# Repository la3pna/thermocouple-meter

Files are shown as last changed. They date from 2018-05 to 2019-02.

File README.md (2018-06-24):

View this project on [CADLAB.io](https://cadlab.io/project/1066). 

# thermocouple-meter
a open source thermocouple meter

This project runs on the Empyrean series ARM microcontroller boards. It may run on Arduino Zero and other SAMD series, but it will not run on ATMEGA series boards!

Todo:
PCB:
* do a PCB for the 2 sensors 3 and 4
* ESP-01 wlan alternative? (as of now there is a extra serial on the board.)
* GPIB? (using the extra serial port?)

SCPI Commands:
   *  *IDN?                  -> identify
   *  *RST                   -> reset to local
   *  :TRIGger
       *    :SINGle          -> trigger single
       *    :CONTinous       -> trigger continous
   *  :MEASure
       *    :TEMPerature?    -> get all temp
       *    :TEMPerature1?   -> get temp1
       *    :TEMPerature2?   -> get temp2
       *    :TEMPerature3?   -> get temp3
       *    :TEMPerature4?   -> get temp4
       *    :INTernal1?      -> get int1 (compensation temperature)
       *    :INTernal2?      -> get int2
       *    :INTernal3?      -> get int3
       *    :INTernal4?      -> get int4
   *  :SYStem
       *    :VOLTage?        -> get supply voltage
       *    :ERRor?          -> get/clears error from error handling
       *    :PRINT           -> display print string
   *  :UNIT *(getting these to work will require rewriting the adafruit library from scratch)*
       *    :TEMPerature     -> set_temperature_unit (C/CEL/F/FAR/K/KEL) *NOT IMPLEMENTED YET* 
       *    :TEMPerature?    -> get_temprature unit (C/CEL/F/FAR/K/KEL) *NOT IMPLEMENTED YET*
       
 Libraries needed: 
   - U8g2lib (Available in arduino library manager)
   - Open Instrument control [scpiparser] ( https://github.com/la3pna/oic )
   - Adafruit MAX31855 (available in arduino library manager) (intend to rewrite this to use some SAMD features in getting the data) 
   
   Bevare that there is some fake MAX31855 on the marked that does not work! Make sure you get your MAX31855 and thermocouples from a reputable source to avoid problems.

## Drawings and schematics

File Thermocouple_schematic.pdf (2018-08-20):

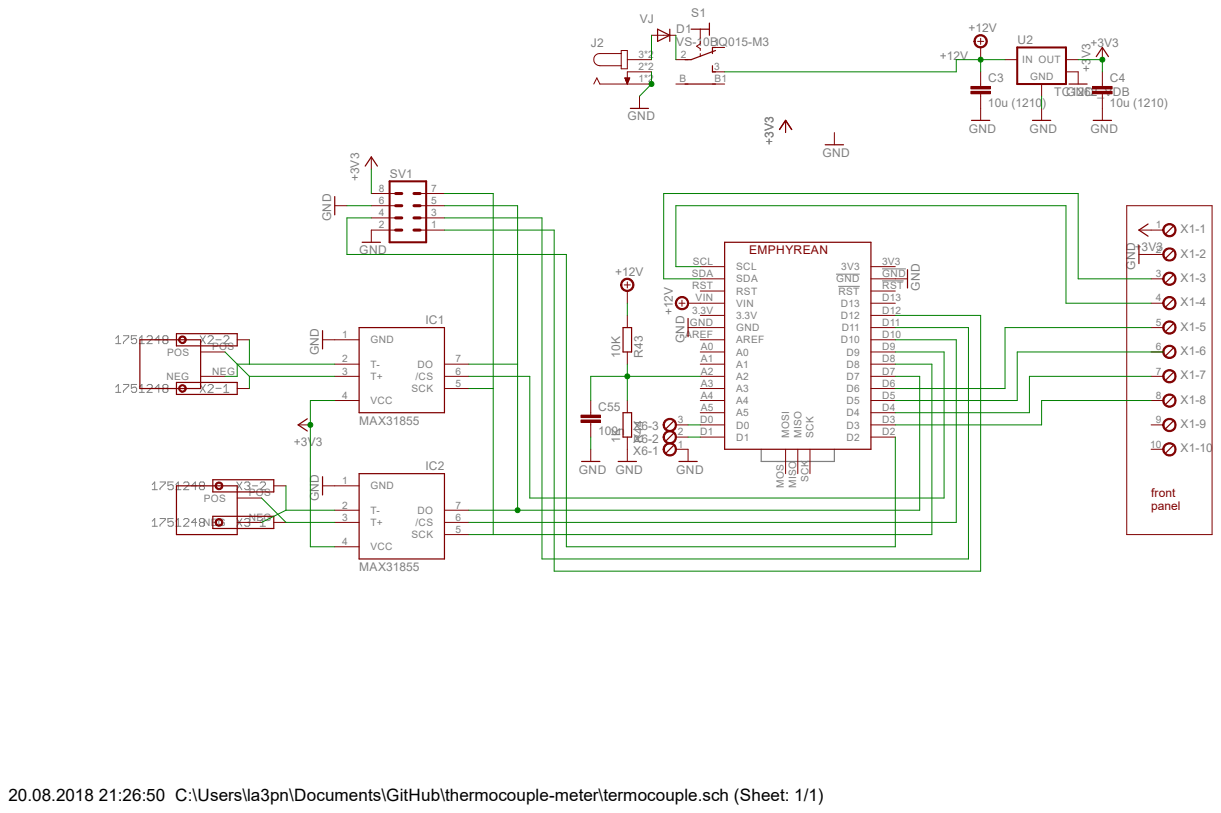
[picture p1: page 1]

20.08.2018 21:26:50 C:\Users\la3pn\Documents\GitHub\thermocouple-meter\termocouple.sch (Sheet: 1/1)

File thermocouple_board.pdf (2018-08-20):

44.45

22.86

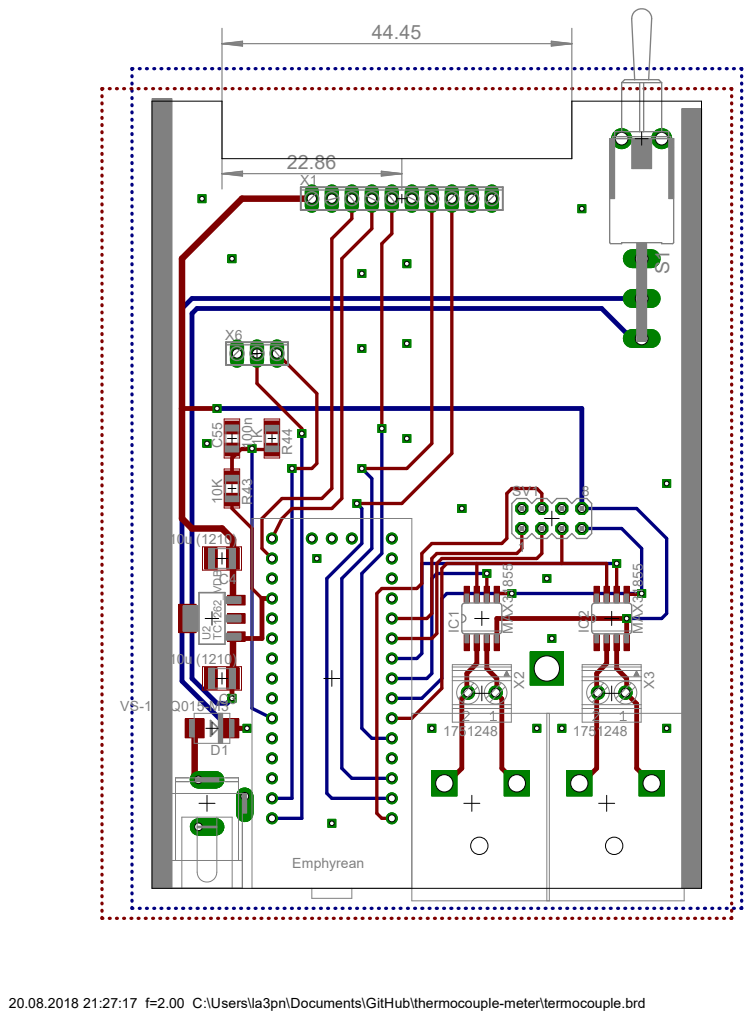
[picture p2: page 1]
Emphyrean; 8 IC¹; IC²; X1 R⁴³; R⁴⁴ C⁵⁵ U²; SV1 MAX³¹⁸⁵⁵; MAX³¹⁸⁵⁵ ¹⁰K; 100n 1K TC¹²⁶²_VDB

20.08.2018 21:27:17 f=2.00 C:\Users\la3pn\Documents\GitHub\thermocouple-meter\termocouple.brd

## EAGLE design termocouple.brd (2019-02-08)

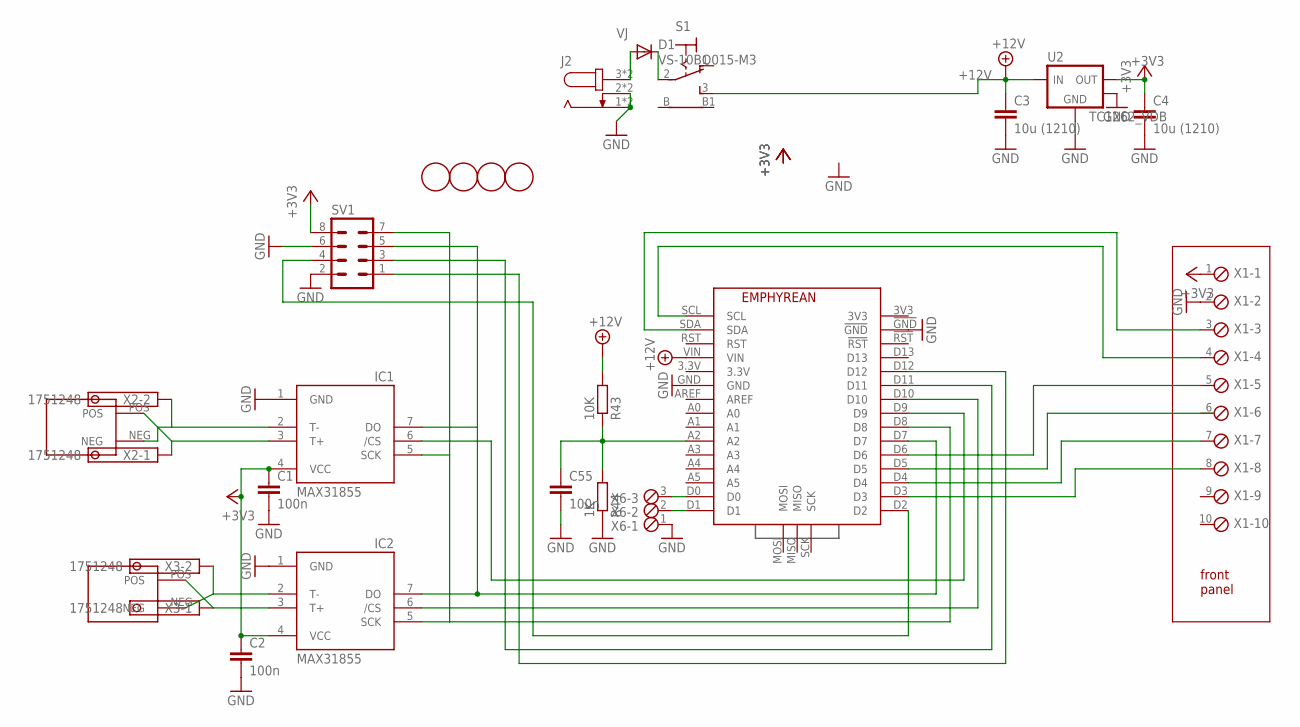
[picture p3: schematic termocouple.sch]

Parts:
C1, C2, C55: 100n; C1206
C3, C4: 10u (1210); C1210
D1: VS-10BQ015-M3; SMB
IC1, IC2: MAX31855; SO08
J2: JACK-PLUG; SPC4078
R43: 10K; R1206
R44: 1K; R1206
S1: LPV-1
SV1: MA04-2
U2: TC1262_VDB; SOT-223-3
U$1: EPHYREAN; EMPHYREAN
U$2, U$3: THERMOCOUPLE
U$4, U$5, U$6, U$7: FIDUCIAL; FIDUCIAL_1MM
X1: MPT10; 10POL254
X2, X3: 1751248
X6: MPT3; 3POL254

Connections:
+3V3: C1.1, C2.1, C4.1, IC1.4 (VCC), IC2.4 (VCC), SV1.8, U2.3 (VOUT), X1.1
+12V: C3.1, R43.2, S1.3 (S), U2.1 (VIN), U$1.VIN
GND: C1.2, C2.2, C3.2, C4.2, C55.2, IC1.1 (GND), IC2.1 (GND), J2.1, J2.2, J2.4 (1), J2.5 (2), R44.1, SV1.2, SV1.6, U2.2 (GND), U2.4 (TAB), U$1.!GND, U$1.GND, X1.2, X6.1
unnamed: IC1.7 (DO), IC2.7 (DO), SV1.5, U$1.D7
unnamed: IC1.5 (SCK), IC2.5 (SCK), SV1.7, U$1.D8
unnamed: IC2.6 (/CS), U$1.D10
unnamed: IC1.6 (/CS), U$1.D9
unnamed: U$1.SDA, X1.3
unnamed: SV1.3, U$1.D11
unnamed: U$1.SCL, X1.4
unnamed: U$1.D6, X1.5
unnamed: U$1.D4, X1.7
unnamed: U$1.D3, X1.8
unnamed: D1.C, S1.2
unnamed: SV1.1, U$1.D12
unnamed: SV1.4, U$1.D2
unnamed: IC2.3 (T+), U$2.POS, X3.1
unnamed: IC2.2 (T-), U$2.NEG, X3.2
unnamed: IC1.3 (T+), U$3.POS, X2.1
unnamed: IC1.2 (T-), U$3.NEG, X2.2
unnamed: U$1.D0, X6.3
unnamed: U$1.D1, X6.2
unnamed: C55.1, R43.1, R44.2, U$1.A2
VJ: D1.A, J2.3, J2.6 (3)

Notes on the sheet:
front panel

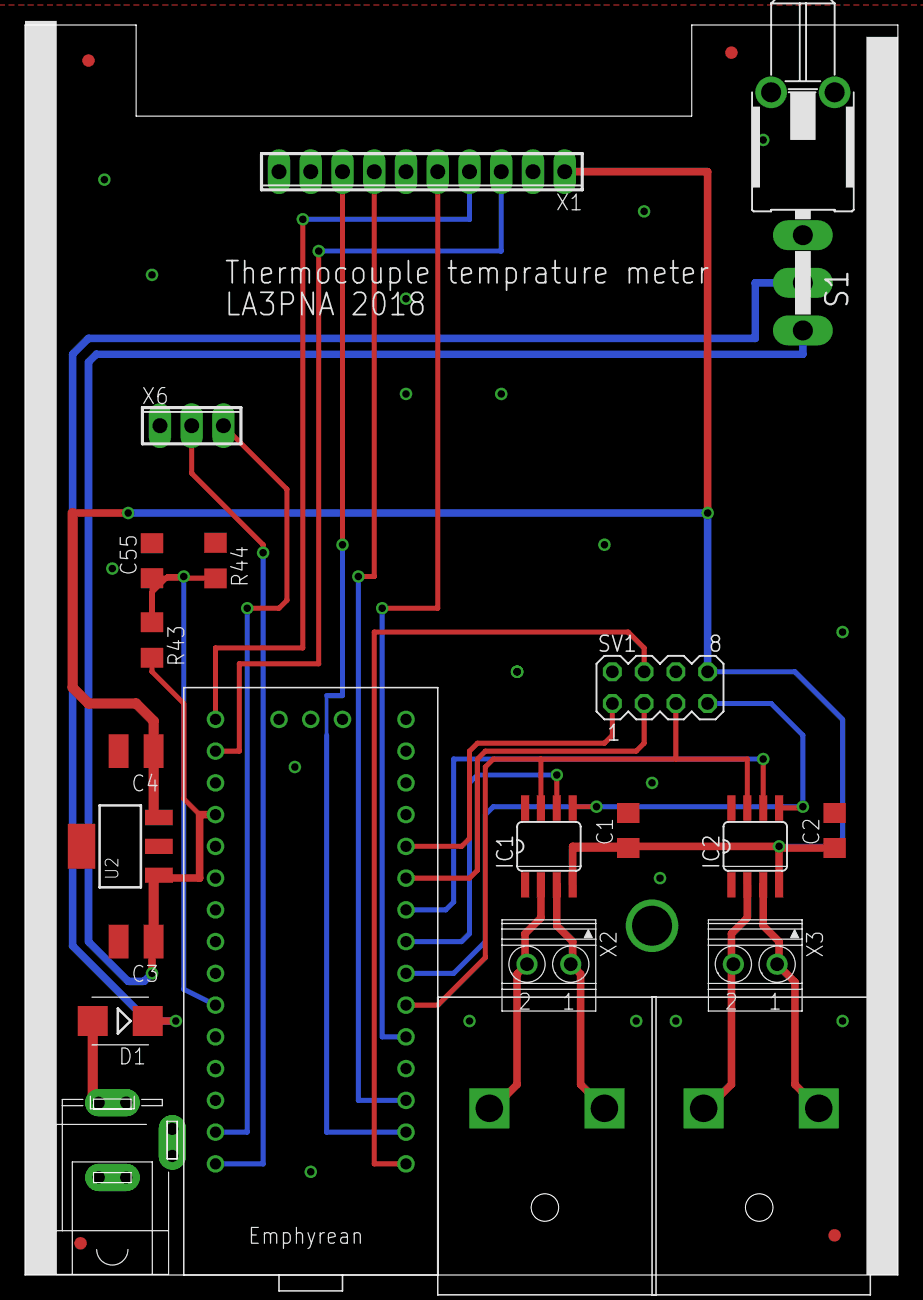
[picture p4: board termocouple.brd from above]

Board: 2 copper layers, 69.8 x 100.0 mm, 25 parts (0 on the bottom side), 24 nets.

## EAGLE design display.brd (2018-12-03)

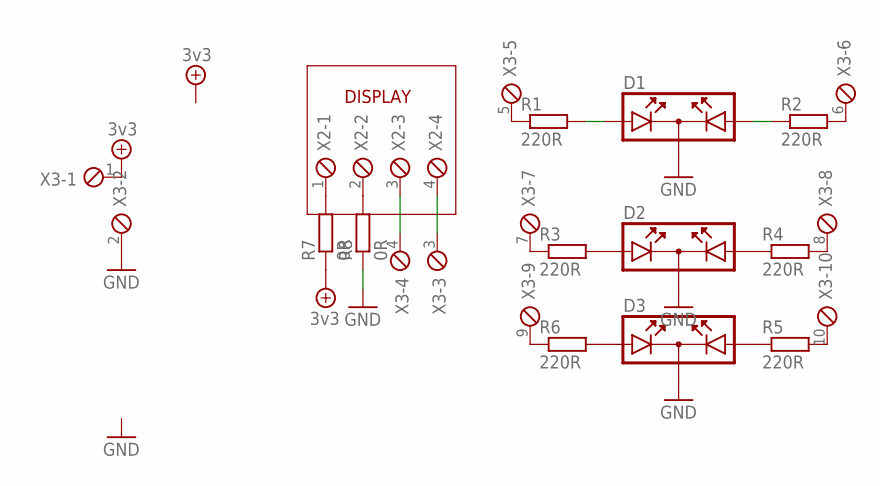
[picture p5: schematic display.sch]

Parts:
D1, D2, D3: DUOLED
R1, R2, R3, R4, R5, R6: 220R; R0603
R7, R8: 0R; R0603
X2: MPT4; 4POL254
X3: MPT10; 10POL254

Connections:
+UB: R7.1, X3.1
GND: D1.K, D2.K, D3.K, R8.1, X3.2
unnamed: D1.A1, R1.2
unnamed: D1.A2, R2.1
unnamed: X2.3, X3.4
unnamed: X2.4, X3.3
unnamed: R1.1, X3.5
unnamed: R2.2, X3.6
unnamed: D2.A1, R3.2
unnamed: D2.A2, R4.1
unnamed: D3.A2, R5.1
unnamed: D3.A1, R6.2
unnamed: R3.1, X3.7
unnamed: R4.2, X3.8
unnamed: R6.1, X3.9
unnamed: R5.2, X3.10
unnamed: R7.2, X2.1
unnamed: R8.2, X2.2

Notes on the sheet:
DISPLAY

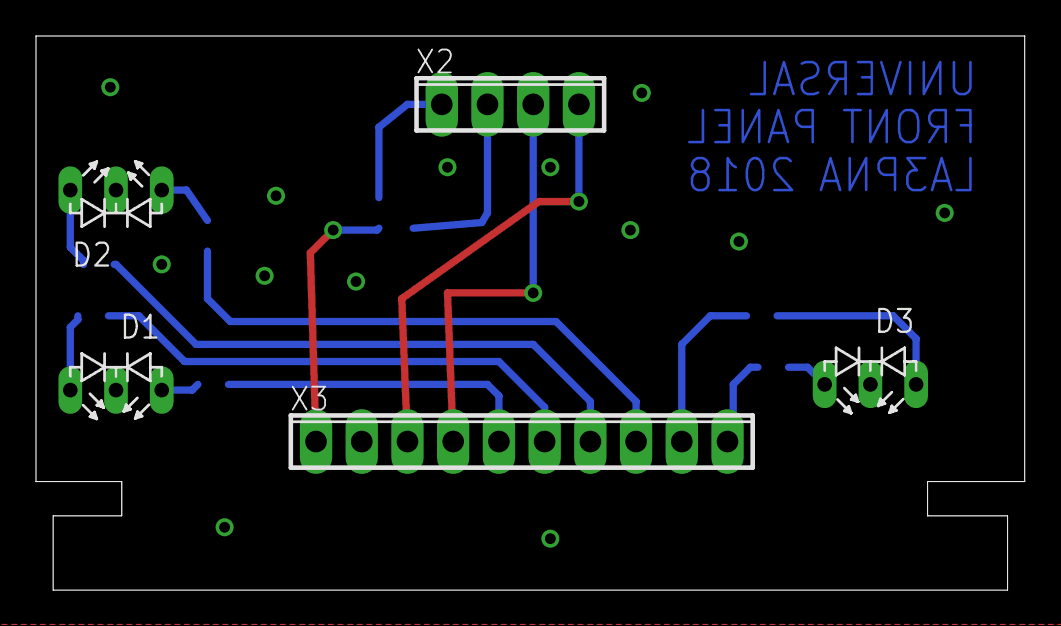
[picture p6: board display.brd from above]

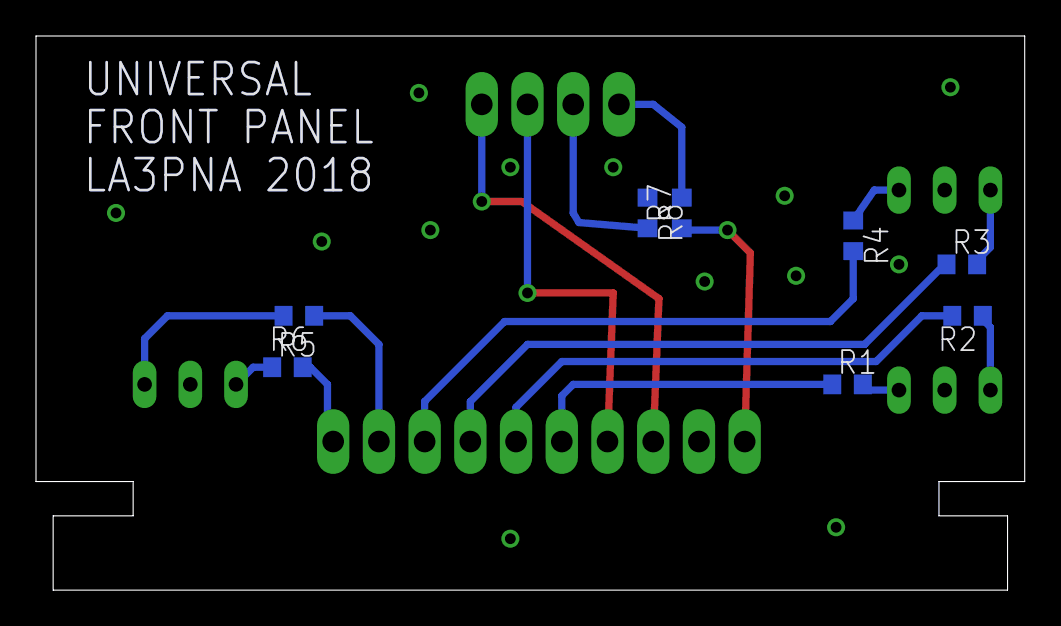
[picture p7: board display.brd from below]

Board: 2 copper layers, 54.9 x 30.8 mm, 13 parts (8 on the bottom side), 18 nets.

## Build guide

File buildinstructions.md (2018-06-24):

**Build instructions**

The PCB fits the standard chinese 100 * 76 * 35mm aluminium enclosures available on ebay. 
PCB's and front panels may be available from me, contact me for information. 

* Mount and solder the SMD's on the main PCB. 
* Mount and solder the socket for the SV1 Expantion port if you intend to build the 4 probe version. 
* Fit the 2 thermocouple connectors to the PCB. 
  - Start by opening the connector and remove all screws and nuts. 
  - Mount the connectors to the PCB using 2 M2 screws and the nuts. The screws goes from the connection tab, via the connector and through the PCB. The nut is fitted on the bottom of the PCB. 
* Mount the backpanel to the bottom part of the enclosure. This is to make sure the alignments are correct.
* Fit the headers to the bottom of the PCB. If your Empyrean comes with the headers fitted, skip this step.
* Mount the Empyrean to the top of the PCB, Do not solder it yet.
* Mount the powerjack, but do not solder it yet.  
* Fit the whole PCB assembly into the board, and see that the connectors fits as it should. 
* Adjust the powerjack and Empyrean PCB so that their connectors fit correctly then solder them to the PCB.
* Add the 2 resistors just below the display to the front panel boards. These determine the power connections to the display.
* Solder the angled row connector to the main PCB.
* Slide the display PCB onto the main PCB and solder it in place.
* Mount the power switch to the PCB, but only solder the end pin.
* Cut the display connector row on the solder side so that it does not protude in front of the display. This is to avoid it shorting to the front panel. 
* Mount the display, but do not solder yet.
* Slide the PCB back into the bottom part of the box, and mount the font panel.  
* Holding the display in its connector, adjust it so that it's position is correct, then tack it down and adjust it so its position is correct on the front panel.
* Solder the display and power switch to the PCB.
* Its time to upload the program and test that it works as it should.

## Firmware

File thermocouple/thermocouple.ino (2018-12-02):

/*
 * Thermocouple SCPI Meter by Thomas S. Knutsen LA3PNA. 
 * 
 * 
 * 
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
 */
 
 #include <U8g2lib.h>
 #include <U8x8lib.h>
 #include <avr/dtostrf.h>
 #include <SPI.h>
  #include <scpiparser.h>
 #include "Adafruit_MAX31855.h"

// In this list you define the input voltage resistors in ohm so it measures the input voltage correctly:
float r44 = 2700; // resistor to gnd
float r43 = 30100; // resistor to Vin
 
 
    #define DO   7
    #define CS1   10
    #define CS2   9
    #define CS3   11
    #define CS4   12
    #define CLK  8
    
#if (!defined(__SAMD21G18A__) && !defined(__SAMD21G16A__) && !defined(__SAMD21G16B__) && !defined(__SAMD21J18A__) && !defined(__SAMD21E17A__) && !defined(__SAMD21E18A__))
 #error "This program will only work on SAMD series boards like Empyrean and Zero"
#endif
    
    Adafruit_MAX31855 thermocouple1(CLK, CS1, DO);
    Adafruit_MAX31855 thermocouple2(CLK, CS2, DO);
    Adafruit_MAX31855 thermocouple3(CLK, CS3, DO);
    Adafruit_MAX31855 thermocouple4(CLK, CS4, DO);
    

    
U8G2_SSD1306_128X32_UNIVISION_1_HW_I2C u8g2(U8G2_R0, /* reset=*/ U8X8_PIN_NONE, /* clock=*/ SCL, /* data=*/ SDA);   // pin remapping with ESP8266 HW I2C

struct scpi_parser_context ctx;

scpi_error_t identify(struct scpi_parser_context* context, struct scpi_token* command);
scpi_error_t reset(struct scpi_parser_context* context, struct scpi_token* command);
scpi_error_t get_voltage(struct scpi_parser_context* context, struct scpi_token* command);
scpi_error_t get_temp_1(struct scpi_parser_context* context, struct scpi_token* command);
scpi_error_t get_temp_2(struct scpi_parser_context* context, struct scpi_token* command);
scpi_error_t get_temp_3(struct scpi_parser_context* context, struct scpi_token* command);
scpi_error_t get_temp_4(struct scpi_parser_context* context, struct scpi_token* command);
scpi_error_t set_voltage_2(struct scpi_parser_context* context, struct scpi_token* command);

  float temp1;
  float temp2;
  float temp3;
  float temp4;
 
  boolean contTrigger = true;
  String idString = "LA3PNA,Thermocouple temperature meter,1,0.1A";
  String sendresponse = "";
  String errorstring = "";
  boolean use2 = false;
  int selectpin = 2;
  boolean _verbose = false;

void draw(float temp1, float temp2, float temp3, float temp4 ) {
  // graphic commands to redraw the complete screen should be placed here

  u8g2.firstPage();
  do {
    u8g2.setFont(u8g2_font_ncenB10_tr);
    char buf[12] ="";
    if(use2){
     u8g2.drawStr(0,25,dtostrf(temp1, 4, 2, buf));
    u8g2.drawStr(70,25,dtostrf(temp2, 4, 2, buf));
    u8g2.setFont(u8g2_font_ncenB08_tr);
    u8g2.drawStr(0,8,"1:");
    u8g2.drawStr(70,8,"2:");
    } else{
     u8g2.drawStr(0,14,dtostrf(temp1, 5, 2, buf));
    u8g2.drawStr(70,14,dtostrf(temp2, 5, 2, buf));
    u8g2.drawStr(0,31,dtostrf(temp3, 5, 2, buf));
    u8g2.drawStr(70,31,dtostrf(temp4, 5, 2, buf));
    }
  } while ( u8g2.nextPage() );
}


 
    void setup() {

      pinMode(selectpin,INPUT);
      digitalWrite(selectpin,HIGH); // put on the pullups
      delay(10);
      if(digitalRead(selectpin))
      {
        use2 = true; // select between 2 and 4 sensors
        }
      
      setup_scpi();
       SerialUSB.begin(9600);
       SerialUSB.println("MAX31855 test");
       // wait for MAX chip to stabilize
       Serial1.begin(115200);
       u8g2.begin();
       delay(500);
    }
    
  char line_buffer[256];
  unsigned char read_length;
  int serialport = 0; // 1 = USB, 2 = Serial1, 3 = Serial5;
    
    void loop() {

    // Here we need a routine that selects between the different serial ports, and does some housekeeping so things goes to the correct place
    //
      if (SerialUSB.available() > 0)   // see if incoming serial data:
  { 
    read_length = SerialUSB.readBytesUntil('\n', line_buffer, 256);
    serialport = 1; // 1 for USB
 
  }
      if (Serial1.available() > 0)   // see if incoming serial data:
  { 
    read_length = Serial1.readBytesUntil('\n', line_buffer, 256);
    serialport = 2; // 2 for wlan/gpib

  }

    if(read_length > 0)
    {
       
      scpi_execute_command(&ctx, line_buffer, read_length);
      read_length = NULL;
    }
      
       // Initialize variables.
        // Counter for arrays
       double internalTemp1 = thermocouple1.readInternal(); // Read the internal temperature of the MAX31855.
       double rawTemp1 = thermocouple1.readCelsius(); // Read the temperature of the thermocouple. This temp is compensated for cold junction temperature.
       
  double  correctedTemp = rawTemp1; // calc_temp(internalTemp1, rawTemp1);
 if(_verbose){  
  SerialUSB.print("Corrected Temp1 = ");
          SerialUSB.print(correctedTemp, 5);
          SerialUSB.print(" internal temp: ");
          SerialUSB.print(internalTemp1, 5);
          SerialUSB.print(" raw temp: ");
          SerialUSB.print(rawTemp1, 5);
          SerialUSB.print(" err: ");
          SerialUSB.println(thermocouple1.readError());
 }    
          
       double    internalTemp2 = thermocouple2.readInternal(); // Read the internal temperature of the MAX31855.
      double  rawTemp2 = thermocouple2.readCelsius(); // Read the temperature of the thermocouple. This temp is compensated for cold junction temperature.
       
   correctedTemp = rawTemp2;// calc_temp(internalTemp, rawTemp);
 if(_verbose){  
  SerialUSB.print("Corrected Temp2 = ");
          SerialUSB.print(correctedTemp, 5);
          SerialUSB.print(" internal temp: ");
          SerialUSB.print(internalTemp2, 5);
          SerialUSB.print(" raw temp: ");
          SerialUSB.print(rawTemp2, 5);
         SerialUSB.print(" err: ");
          SerialUSB.print(thermocouple2.readError());
          SerialUSB.print("  ");
           SerialUSB.print(" analog A0:");
           
            
              float volt = analogRead(A0)*((47+5700)/47)*(3.3/1024);
              SerialUSB.println(volt);
              SerialUSB.println(contTrigger);

    }

  if(contTrigger){            
if(use2){        
 draw( rawTemp1, rawTemp2, internalTemp1, internalTemp2);
} else{
 draw( rawTemp1, rawTemp2, NAN, NAN);
}
  }
     //  delay(1000);
 
    }
    

void setup_scpi(){
  
  struct scpi_command* trigger;
  struct scpi_command* measure;
  struct scpi_command* systems;
  struct scpi_command* unit;
  
  /* First, initialise the parser. */
  scpi_init(&ctx);

  /*
   * After initialising the parser, we set up the command tree.  Ours is
   *
   *  *IDN?         -> identify
   *  *RST          -> reset to local
   *  :TRIGger
   *    :SINGle    -> trig_single
   *    :CONTinous   -> trig_cont
   *  :MEASure
   *    :TEMPerature?   -> get_alltemp
   *    :TEMPerature1?   -> get_temp1
   *    :TEMPerature2?   -> get_temp2
   *    :TEMPerature3?   -> get_temp3
   *    :TEMPerature4?   -> get_temp4
   *    :INTernal1?      -> get_int1
   *    :INTernal2?      -> get_int2
   *    :INTernal3?      -> get_int3
   *    :INTernal4?      -> get_int4
   *  :SYStem
   *    :VOLTage?   -> get_voltage
   *  :UNIT
   *    :TEMPerature -> set_temperature_unit (C/CEL/F/FAR/K/KEL)
   *    :TEMPerature? -> get_temprature unit (C/CEL/F/FAR/K/KEL)
   */
  scpi_register_command(ctx.command_tree, SCPI_CL_SAMELEVEL, "*IDN?", 5, "*IDN?", 5, identify);
  scpi_register_command(ctx.command_tree, SCPI_CL_SAMELEVEL, "*RST", 4, "*RST", 4, reset);

  trigger = scpi_register_command(ctx.command_tree, SCPI_CL_CHILD, "TRIGger", 7, "TRIG", 4, NULL);
  measure = scpi_register_command(ctx.command_tree, SCPI_CL_CHILD, "MEASure", 7, "MEAS", 4, NULL);
  systems = scpi_register_command(ctx.command_tree, SCPI_CL_CHILD, "SYStem", 6, "SYS", 3, NULL);
  unit = scpi_register_command(ctx.command_tree, SCPI_CL_CHILD, "UNIT", 4, "UNIT", 4, NULL);


  scpi_register_command(trigger, SCPI_CL_CHILD, "SINGle", 6, "SING", 4, trig_single);
  scpi_register_command(trigger, SCPI_CL_CHILD, "CONTinous", 9, "CONT", 4, trig_cont);

  scpi_register_command(measure, SCPI_CL_CHILD, "VOLTAGE?", 8, "VOLT?", 5, get_voltage); //this works?
  scpi_register_command(measure, SCPI_CL_CHILD, "TEMPerature?", 12, "TEMP?", 5, get_temp);
  scpi_register_command(measure, SCPI_CL_CHILD, "TEMPerature1?", 13, "TEMP1?", 6, get_temp1);
  scpi_register_command(measure, SCPI_CL_CHILD, "TEMPerature2?", 13, "TEMP2?", 6, get_temp2);
  
  scpi_register_command(measure, SCPI_CL_CHILD, "INTernal1?", 10, "INT1?", 5, get_int1);
  scpi_register_command(measure, SCPI_CL_CHILD, "INTernal2?", 10, "INT2?", 5, get_int2);
  
  // NEED A DEFINE FOR 4 MEASUREMENTS, NEED TO IMPLEMENT THE SWITCHING IN SETUP
if(!use2){
  scpi_register_command(measure, SCPI_CL_CHILD, "TEMPerature3?", 13, "TEMP3?", 6, get_temp3);
  scpi_register_command(measure, SCPI_CL_CHILD, "TEMPerature4?", 13, "TEMP4?", 6, get_temp4);
  scpi_register_command(measure, SCPI_CL_CHILD, "INTernal3?", 10, "INT3?", 5, get_int3);
  scpi_register_command(measure, SCPI_CL_CHILD, "INTernal4?", 10, "INT4?", 5, get_int4);
}

  scpi_register_command(systems, SCPI_CL_CHILD, "ERRor?", 6, "ERR?", 4, get_err);
  scpi_register_command(systems, SCPI_CL_CHILD, "VOLTage?", 8, "VOLT?", 5, get_voltage); 
  scpi_register_command(systems, SCPI_CL_CHILD, "PRINT", 5, "PRINT", 5, display_print); 
  }

  // from here down is the different command definitions.

  scpi_error_t identify(struct scpi_parser_context* context, struct scpi_token* command)
{
  scpi_free_tokens(command);
if(serialport == 1){
  SerialUSB.println(idString);
} else if (serialport == 2){
  Serial1.println(idString);
  }else if (serialport == 3){
    Serial.println(idString);
    }else{
      }
   serialport = 0; // 2 for wlan/gpib
  return SCPI_SUCCESS;
}

scpi_error_t reset(struct scpi_parser_context* context, struct scpi_token* command)
{
if(serialport == 1){
  sendresponse = "Resetting ";
  
  SerialUSB.println(sendresponse);
} else if (serialport == 2){
  Serial1.println(sendresponse);
  }else if (serialport == 3){
    Serial.println(sendresponse);
    }else{
      }
   serialport = 0; // 2 for wlan/gpib
   sendresponse = "";
   
  scpi_free_tokens(command);
   NVIC_SystemReset();
  return SCPI_SUCCESS;
}

 scpi_error_t trig_single(struct scpi_parser_context* context, struct scpi_token* command)
{

  // needs to do a single trigger here
  scpi_free_tokens(command);
  _verbose = false;
  contTrigger = false;
  return SCPI_SUCCESS;
}
 scpi_error_t trig_cont(struct scpi_parser_context* context, struct scpi_token* command)
{
  scpi_free_tokens(command);

  contTrigger = true;
  _verbose = true;
  return SCPI_SUCCESS;
}

scpi_error_t get_voltage(struct scpi_parser_context* context, struct scpi_token* command)
{
  scpi_free_tokens(command);
  SerialUSB.println("test to see if its a logic fault or this does not run");
  
  float volt = analogRead(A0)*((r44)/(r44+r43))*(3.3/1024);
 float divisor = ((r44)/(r44+r43));
  sendresponse = "Power supply voltage: " + String(volt) + " V";          
if(serialport == 1){
  SerialUSB.println(sendresponse);
} else if (serialport == 2){
  Serial1.println(sendresponse);
  }else if (serialport == 3){
    Serial.println(sendresponse);
    }else{
      errorstring = errorstring + " Error: Unknown port reply";
      }
   serialport = 0; // 2 for wlan/gpib
   sendresponse = "";
              
  return SCPI_SUCCESS;
}

scpi_error_t get_temp(struct scpi_parser_context* context, struct scpi_token* command)
{

if(use2)
{
  sendresponse = String(thermocouple1.readCelsius())+ "; " + String(thermocouple2.readCelsius())+";"; 

  } else 
  { sendresponse = String(thermocouple1.readCelsius())+"; "+String(thermocouple2.readCelsius())+"; "+String(thermocouple3.readCelsius())+"; "+String(thermocouple4.readCelsius())+";"; 

    }
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

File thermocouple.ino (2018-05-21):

#include <SPI.h>
    #include "Adafruit_MAX31855.h"
 
    #define DO   3
    #define CS   4
    #define CLK  5
    Adafruit_MAX31855 thermocouple(CLK, CS, DO);
 
    void setup() {
       SerialUSB.begin(9600);
       SerialUSB.println("MAX31855 test");
       // wait for MAX chip to stabilize
       delay(500);
    }
    void loop() {
       // Initialize variables.
        // Counter for arrays
       double internalTemp = thermocouple.readInternal(); // Read the internal temperature of the MAX31855.
       double rawTemp = thermocouple.readCelsius(); // Read the temperature of the thermocouple. This temp is compensated for cold junction temperature.
       
  double  correctedTemp =  calc_temp(internalTemp, rawTemp);
 
  SerialUSB.print("Corrected Temp = ");
          SerialUSB.println(correctedTemp, 5);
          SerialUSB.println("");
 
       delay(1000);
 
    }

    double calc_temp(double internalTemp,double rawTemp ){

        double thermocoupleVoltage= 0;
       double internalVoltage = 0;
       double correctedTemp = 0;
       double totalVoltage = 0;
       int i = 0;
      
        // Check to make sure thermocouple is working correctly.
       if (isnan(rawTemp)) {
        SerialUSB.println("Something wrong with thermocouple!");
      }
       else {
          // Steps 1 & 2. Subtract cold junction temperature from the raw thermocouple temperature.
          thermocoupleVoltage = (rawTemp - internalTemp)*0.041276;  // C * mv/C = mV
 
          // Step 3. Calculate the cold junction equivalent thermocouple voltage.
 
          if (internalTemp >= 0) { // For positive temperatures use appropriate NIST coefficients
             // Coefficients and equations available from http://srdata.nist.gov/its90/download/type_k.tab
 
             double c[] = {-0.176004136860E-01,  0.389212049750E-01,  0.185587700320E-04, -0.994575928740E-07,  0.318409457190E-09, -0.560728448890E-12,  0.560750590590E-15, -0.320207200030E-18,  0.971511471520E-22, -0.121047212750E-25};
 
             // Count the the number of coefficients. There are 10 coefficients for positive temperatures (plus three exponential coefficients),
             // but there are 11 coefficients for negative temperatures.
             int cLength = sizeof(c) / sizeof(c[0]);
 
             // Exponential coefficients. Only used for positive temperatures.
             double a0 =  0.118597600000E+00;
             double a1 = -0.118343200000E-03;
             double a2 =  0.126968600000E+03;
 
 
             // From NIST: E = sum(i=0 to n) c_i t^i + a0 exp(a1 (t - a2)^2), where E is the thermocouple voltage in mV and t is the temperature in degrees C.
             // In this case, E is the cold junction equivalent thermocouple voltage.
             // Alternative form: C0 + C1*internalTemp + C2*internalTemp^2 + C3*internalTemp^3 + ... + C10*internaltemp^10 + A0*e^(A1*(internalTemp - A2)^2)
             // This loop sums up the c_i t^i components.
             for (i = 0; i < cLength; i++) {
                internalVoltage += c[i] * pow(internalTemp, i);
             }
                // This section adds the a0 exp(a1 (t - a2)^2) components.
                internalVoltage += a0 * exp(a1 * pow((internalTemp - a2), 2));
          }
          else if (internalTemp < 0) { // for negative temperatures
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

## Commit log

2018-05-21 eagle files
    [termocouple.brd, termocouple.sch]
2018-05-21 arduino program
2018-05-21 update brd
    [termocouple.brd]
2018-05-21 sch update
    [termocouple.sch]
2018-05-21 brd
    power supply measuring, should do somthing with the rest of the adc pins?
    [termocouple.brd]
2018-05-21 wiring change
    [termocouple.brd, termocouple.sch]
2018-05-21 front panel + brd traces
    [display.brd, display.sch, termocouple.brd, termocouple.sch]
2018-05-22 FW: changes in font and printing
2018-05-22 BRD added thermocouple device
    thermocouple
    [termocouple.brd, termocouple.sch]
2018-05-24 readme update, arm definitions, pcb moved to 2 sensor
    [termocouple.brd, termocouple.sch]
2018-05-27 updated brd
    finished routing PCB
    [termocouple.brd]
2018-05-29 front panel board made to fit
    [display.brd, display.sch, termocouple.brd]
2018-06-01 fix switching between 2 and 4 sensors
2018-06-01 small rework to remove the sensor 3 and 4 SCPI from a board with 2 sensors
2018-06-01 print routine added
2018-08-20 pdf version of schematics
    [termocouple.brd, termocouple.sch]
2018-12-02 pcb fix
    Fix PCB's to make it possible to build the boards without rework
    [display.brd, termocouple.brd, termocouple.sch]
2018-12-02 program changes
    Add resistor for voltage dividers
2018-12-03 update display.brd and thermocouple
    [display.brd, termocouple.brd, termocouple.sch]
2019-02-08 pcb add fiducials
    [termocouple.brd, termocouple.sch]
